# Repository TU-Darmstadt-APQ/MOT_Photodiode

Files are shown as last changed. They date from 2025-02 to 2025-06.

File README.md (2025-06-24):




# MOT Photodiode
This is a photodiode board with a transimpedance amplifier for [S-100](https://osioptoelectronics.com/media/pages/products/photodetectors/solderable-chip-photodiodes/s-100vl/1aa00dfa44-1675100439/solderable-chips.pdf) photodiodes used to probe the MOT beams at the QUIPS-C experiment.
The photodiode is inserted into the laser beam on a slide-in unit ([slide_in_mount](photodiode_mount/slide_in_mount.ipt) in combination with the [photo_plate_slide_in](photodiode_mount/photo_plate_slide_in.ipt)) which can be placed behind the MOT Beam Doublett collimators. This assembly is mounted on a flange screwed to the vacuum chamber (viewport_mount assembly designed by Lars Pause). The photodiode board can be screwed on this holder with two polymer screws. 

## Contents
- [Introduction](#introduction)
- [Design files](#design-files)
- [Related repositories](#related-repositories)
- [Versioning](#versioning)
- [License](#license)

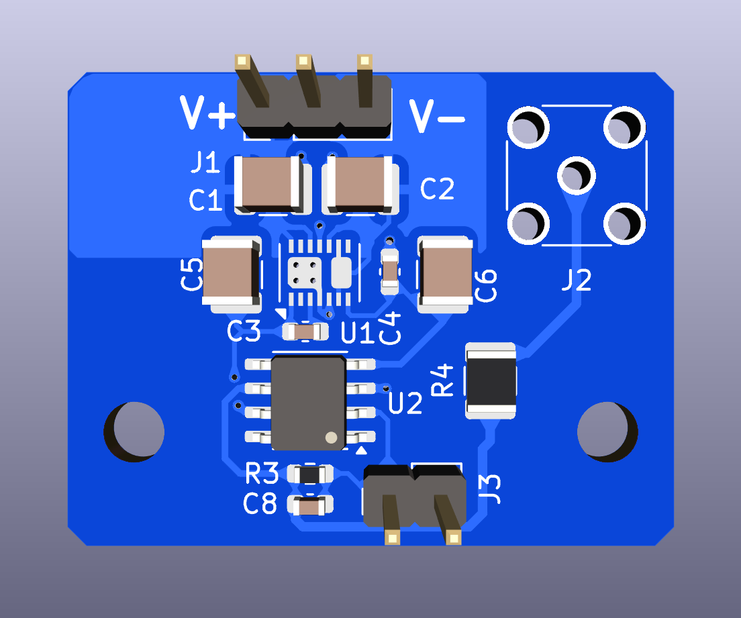
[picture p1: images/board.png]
DVI connector pin layout


## Introduction
The photodiode board features a single-stage amplifier and a voltage regulator to power the op-amp. The power supply required needs to provide +-15 V via a pin header. The bandwidth of the system is about 10 kHz. For details see [here](datasheet/bandwidth.png).

## Design files
### For production
The design files required for the PCB production and assembly can be found on the [releases](../../releases) page and include the following resources:

- Schematics as a PDF
- Gerber files
- Pick & place position files
- Bill of materials as a CSV file and also as an interactive HTML version
- Mechanical design files for manufacturing the housing as PDF

The latest revision of those files can be found [here](../../releases/latest).

### For editing
To work on the [KiCad](https://www.kicad.org/) design files, a number of external libraries are needed. Those libraries show up as empty folders in the zip file, because they are not included in the release, but must be downloaded separately from the links given [below](#related-repositories). This can be avoided by checking out the whole repository using git. This way the libraries will be downloaded as well. Use the following command to clone the git repository along with the submodules  using the `--recurse-submodules` flag.
```
git clone --recurse-submodules https://github.com/TU-Darmstadt-APQ/MOT_Photodiode.git
```

## Related repositories
See the following repositories for more information as these are part of the [design files](#design Files).

- [KiCad footprints](https://github.com/PatrickBaus/footprints.pretty)
- [KiCAD 3D models](https://github.com/PatrickBaus/footprints.3dshapes)
- [KiCAD schematic libraries](https://github.com/PatrickBaus/KiCad-libraries)

## Versioning
I use [SemVer](http://semver.org/) for versioning. For the versions available, see the [tags](../../tags) available for this repository.

- MAJOR versions in this context mean a breaking change to the external interface of the hardware like different connectors or functions.
- MINOR versions contain changes to the hardware that only affect the inner workings of the circuit, but otherwise the performance is unaffected.
- PATCH versions do not affect the schematics or invalidate older bill of materials. These changes may include updated components (to replace obsolete parts for example), an updated silkscreen, or fixed typos.

## License
This work is released under the CERN-OHL-W
See [https://ohwr.org/cern_ohl_w_v2.pdf](https://ohwr.org/cern_ohl_w_v2.pdf) or the included [LICENSE](LICENSE) file for more information.

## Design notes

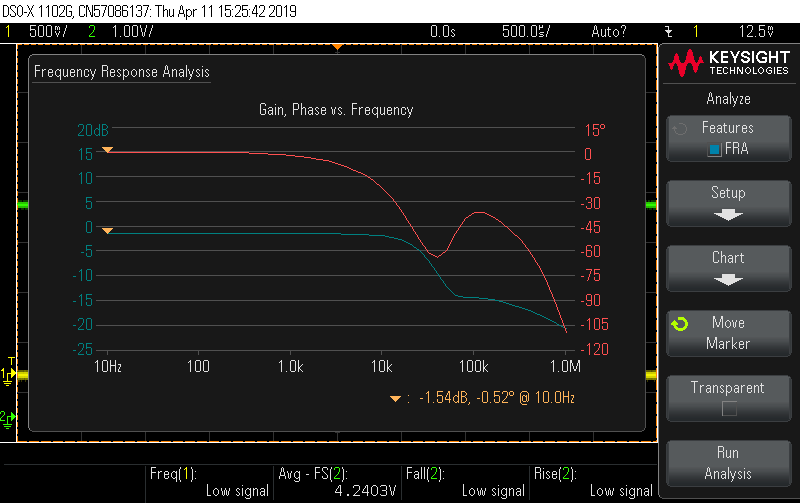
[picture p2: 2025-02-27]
datasheet/bandwidth.png

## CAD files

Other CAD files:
photodiode_mount/photo_plate_slide_in.ipt
photodiode_mount/slide_in_mount.ipt

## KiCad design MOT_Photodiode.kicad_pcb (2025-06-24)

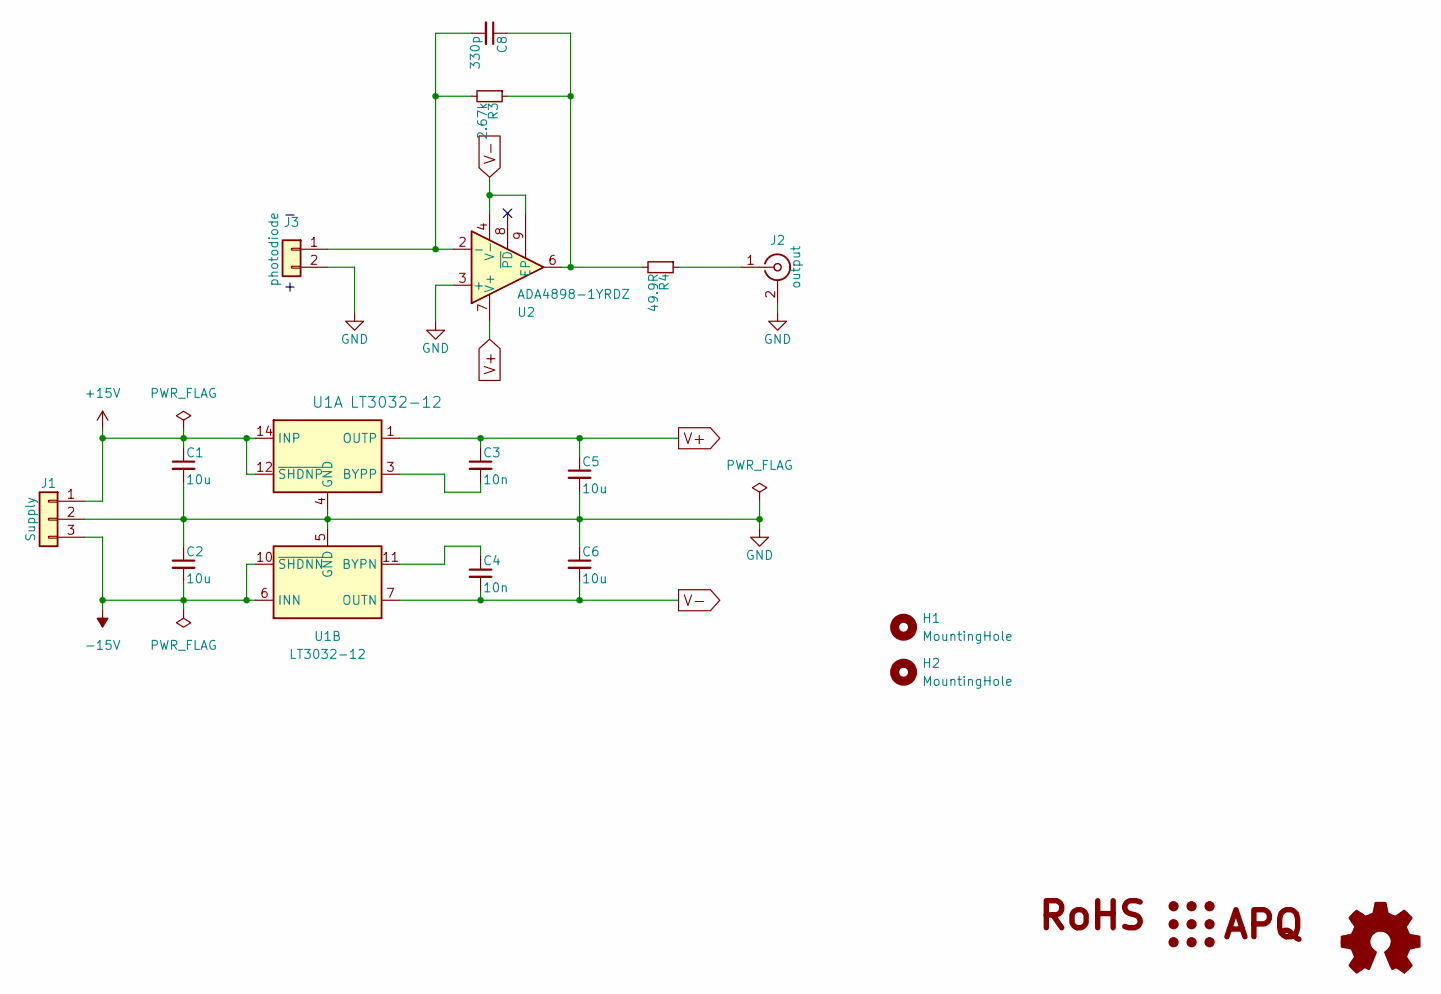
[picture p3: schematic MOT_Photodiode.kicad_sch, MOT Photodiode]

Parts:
C1, C2, C5, C6: 10u; C_1210_3225Metric
C3, C4: 10n; C_0603_1608Metric
C8: 330p; C_0603_1608Metric
H1, H2: MountingHole; MountingHole_3.2mm_M3
J1: Supply; PinHeader_1x03_P2.54mm_Vertical
J2: output; SMA_Amphenol_132134_Vertical
J3: photodiode; PinHeader_1x02_P2.54mm_Vertical
R3: 2.67k; R_0603_1608Metric
R4: 49.9R; R_1210_3225Metric
SYM1: Logo_Open_Hardware_Small; OSHW-Logo_7.5x8mm_SilkScreen
SYM2: Logo_APQ; APQ-Logo_small
U1: LT3032-12; Linear_DE14MA
U2: ADA4898-1YRDZ; SOIC-8-1EP_3.9x4.9mm_P1.27mm_EP2.29x3mm

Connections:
+15V: C1.1, J1.1, U1.12 (~SHDNP), U1.14 (INP)
-15V: C2.2, J1.3, U1.6 (INN), U1.9 (INN), U1.10 (~SHDNN)
GND: C1.2, C2.1, C5.2, C6.1, J1.2, J2.2 (Ext), J3.2, U1.4 (GND), U1.5 (GND), U2.3 (+)
unnamed: C8.1, R3.1, R4.2, U2.6
unnamed: J2.1 (In), R4.1
unnamed: C8.2, J3.1, R3.2, U2.2 (-)
unnamed: C3.2, U1.3 (BYPP)
unnamed: C4.1, U1.11 (BYPN)
V+: C3.1, C5.1, U1.1 (OUTP), U2.7 (V+)
V-: C4.2, C6.2, U1.7 (OUTN), U2.4 (V-), U2.9 (EP)

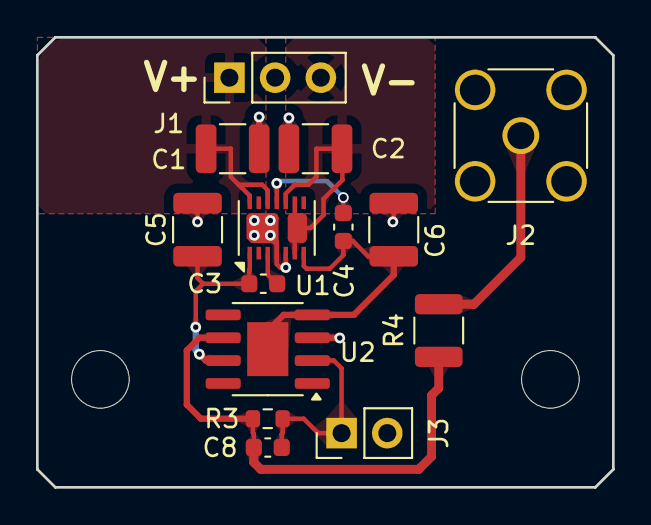
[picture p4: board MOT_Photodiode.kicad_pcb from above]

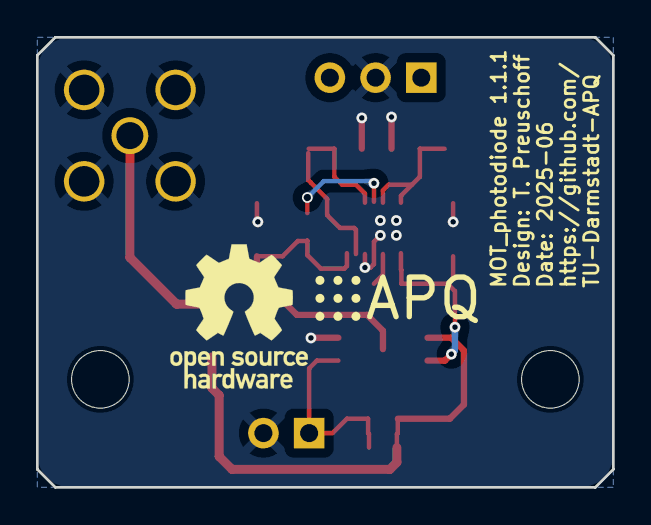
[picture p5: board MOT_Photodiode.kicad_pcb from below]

Board: 2 copper layers, 32.0 x 25.0 mm, 18 parts (2 on the bottom side), 10 nets.

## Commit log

2025-02-27 Added logos
    [MOT_Photodiode.kicad_pcb, MOT_Photodiode.kicad_sch]
2025-02-27 Chamfered corners
    [MOT_Photodiode.kicad_pcb]
2025-02-27 Reduced via drill size from 0.4 mm to 0.3 mm
    [MOT_Photodiode.kicad_pcb]
2025-02-27 Added teardrops
    [MOT_Photodiode.kicad_pcb]
2025-02-27 Added BOM
    [MOT_Photodiode.kicad_pcb, MOT_Photodiode.kicad_sch]
2025-06-24 Update/kicad9 (#2)
    * Update files to KiCad 9 incl. footprint updates
    * Bump CI to KiCad 9
    * Refilled copper pour
    * Bump version to 1.1.1
    [MOT_Photodiode.kicad_pcb, MOT_Photodiode.kicad_sch]
2025-06-24 Updated readme and added mechanical design files (#1)
    * add description
    * add ipt inventor Files
    Original files and whole assembly of viewport_mount can be found on Brain:
    Labortechnik\Mechanik\QUIPS_C\Vakuumkammer_assembly\viewport_flanges
    [photo_plate_slide_in.ipt, slide_in_mount.ipt]

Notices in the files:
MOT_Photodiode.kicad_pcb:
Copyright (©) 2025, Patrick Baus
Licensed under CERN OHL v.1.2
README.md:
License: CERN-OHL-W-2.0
